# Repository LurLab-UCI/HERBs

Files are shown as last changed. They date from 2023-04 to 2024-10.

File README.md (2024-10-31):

# HERBs
Head-fixed Environment for Rodent Behaviors

This is a comprehensive, affordable and highly flexible hardware-software solution for head-fixed behaviors

For installation instructions and documentation see Wiki (https://github.com/LurLab-UCI/HERBs/wiki)

If used, please cite:
https://www.eneuro.org/content/10/6/ENEURO.0018-23.2023.long

**Critical Update Oct 30, 2024**

HERBs 2.0 is realeased with important bug fixes and communication updates
bug fixes:
* fixed a bug that caused stimulus display to be only half of what was defined in GUI
* fixed bug that caused multiple licks to be printed in the same line
* updated serial communicaton to work with new MATLAB releases

It is recomended that all users switch to HERBs 2.0 for correct stimulus duration.

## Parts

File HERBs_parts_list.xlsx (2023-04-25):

 | # per rig (GNG) | # per rig (2AFC) | ~ price | cost (GNG) | cost (2AFC) | vendor | part # | link
arduino
arduino mega | 1 | 1 | 40.3 | 40.3 | 40.3 | Arduino | A000067 | https://store-usa.arduino.cc/products/arduino-mega-2560-rev3?selectedStore=us
arduino DUE | 1 | 1 | 40.3 | 40.3 | 40.3 | arduino | A000062 | https://store-usa.arduino.cc/products/arduino-due
electronics and other parts
capacitative lick detector | 1 | 3 | 6.5 | 6.5 | 19.5 | sparkfun | 14520 | https://www.sparkfun.com/products/14520
capacitor | 1 | 3 | 0.3 | 0.3 | 0.9 | sparkfun | 8375 | https://www.sparkfun.com/products/8375
power control kit | 1 | 3 | 5.95 | 5.95 | 17.85 | sparkfun | 12959 | https://www.sparkfun.com/products/12959
MOSFET chip (alternative power ctrl.) | 1 | 3 | 1.25 | 1.25 | 3.75 | sparkfun | 10213 | https://www.sparkfun.com/products/10213
level converter | 1 | 1 | 3.5 | 3.5 | 3.5 | sparkfun | BOB-12009 | https://www.sparkfun.com/products/12009
10k Ohm resistor | 1 | 3 | 0.025 | 0.025 | 0.075 | sparkfun | 11508 | https://www.sparkfun.com/products/11508
diode rectifier | 1 | 3 | 0.25 | 0.25 | 0.75 | sparkfun | 14884 | https://www.sparkfun.com/products/14884
speakers | 2 | 2 | 2.45 | 4.9 | 4.9 | sparkfun | 9151 | https://www.sparkfun.com/products/9151
1/4 inch hub | 1 | 1 | 4.99 | 4.99 | 4.99 | sparkfun | 12488 | https://www.sparkfun.com/products/12488
LED panels | 3 | 3 | 6.95 | 20.85 | 20.85 | adafruit | 2973 | https://www.adafruit.com/product/2973
LED panel drivers | 3 | 3 | 5.95 | 17.85 | 17.85 | adafruit | 2946 | https://www.adafruit.com/product/2946
audio amp | 1 | 1 | 19.95 | 19.95 | 19.95 | adafruit | MAX9744 | https://www.adafruit.com/product/1752
tubing (if longer range is needed) | 1 | 1 | 86 | 86 | 86 | cole-parmer | EW-06419-04 | https://www.coleparmer.com/i/masterflex-microbore-transfer-tubing-tygon-nd-100-80-0-040-id-x-0-070-od-100-ft/0641904?searchterm=EW-06419-04
solenoid valve | 1 | 3 | 75.78 | 75.78 | 227.34 | reet corp. | 075P2NC12-02S | http://www.reetcorp.com/products-valves.html
1/4 inch shaft ~1.5'' long | 1 | 1 | 9.64 | 9.64 | 9.64 | McMaster | 8632T144 | https://www.mcmaster.com/8632T144/
1/4 bearings | 2 | 2 | 10.98 | 21.96 | 21.96 | McMaster | 4262T36 | https://www.mcmaster.com/4262T36/
1/4'' wheel lock shaft collar | 1 | 1 | 3.1 | 3.1 | 3.1 | McMaster | 9946K11 | https://www.mcmaster.com/9946K11/
12v power supply | 1 | 1 | 6.98 | 6.98 | 6.98 | amazon | generic | https://www.amazon.com/Adapter-SANSUN-AC100-240V-Transformers-Switching/dp/B01AZLA9XQ
9V power supply | 1 | 1 | 9.99 | 9.99 | 9.99 | amazon | generic | https://www.amazon.com/DAddario-PW-CT-9V-Power-Adapter-Sleeve-Positive/dp/B00191WVF6
running wheel | 1 | 1 | 12.99 | 12.99 | 12.99 | amazon | generic | https://www.amazon.com/gp/product/B00ZB3S62K/ref=ppx_yo_dt_b_search_asin_title?ie=UTF8&psc=1
plasti dip (wheel coating) | 1 | 1 | 7.99 | 7.99 | 7.99 | amazon | generic | https://www.amazon.com/Plasti-Dip-11252-6-Spray-Fluid_Ounces/dp/B00KUBKUQ8?cv_ct_cx=plasti+dip
3D arm | 1 | 1 | 31.35 | 31.35 | 31.35 | amazon | generic | https://www.amazon.com/gp/product/B07KPY6ZC3/ref=ppx_yo_dt_b_search_asin_title?ie=UTF8&psc=1
IR webcam | 1 | 1 | 34.99 | 34.99 | 34.99 | amazon | generic | https://www.amazon.com/gp/product/B0829HZ3Q7/ref=ppx_yo_dt_b_search_asin_title?ie=UTF8&psc=1
power strip (8x) | 1 | 1 | 17.97 | 17.97 | 17.97 | amazon | generic | https://www.amazon.com/Protector-Nuetsa-Extension-Outlets-Joules/dp/B09F2XPJ47?s=electronics
PC (core i5, 8gb ram) | 1 | 1 | 500 | 500 | 500 | amazon | any | https://www.amazon.com/Dell-Inspiron-Compact-Tower-Desktop/dp/B09HHMZN4W?s=electronics
small breadboards | 1 | 1 | 9.59 | 9.59 | 9.59 | amazon | generic | https://www.amazon.com/DEYUE-Solderless-Prototype-Breadboard-breadboard/dp/B07DMHVC3R
20awg wire | 1 | 1 | 16.38 | 16.38 | 16.38 | amazon | generic | https://www.amazon.com/gp/product/B083DNGSPV/ref=ppx_yo_dt_b_search_asin_title?ie=UTF8&psc=1
LED goosneck lamp | 1 | 1 | 21.5 | 21.5 | 21.5 | amazon | generic | https://www.amazon.com/gp/product/B07L6T1N1K/ref=ppx_yo_dt_b_search_asin_title?ie=UTF8&psc=1
spout tubing | 1 | 1 | 7.58 | 7.58 | 7.58 | amazon | generic | https://www.amazon.com/gp/product/B004WPQ59O/ref=ppx_yo_dt_b_search_asin_title?ie=UTF8&psc=1
rotary servo | 1 | 2 | 20.99 | 20.99 | 41.98 | amazon | MG90S | https://www.amazon.com/gp/product/B07F7VJQL5/ref=ppx_yo_dt_b_search_asin_title?ie=UTF8&psc=1
linear actuator (optional if not servo) | 1 | 2 | 90 | 90 | 180 | actuonix | L12-30-50-12-I | https://www.actuonix.com/Rod-Actuators-s/1924.htm
mechanical parts
90 degree thumbscrew holder (RA90) | 4 | 4 | 10.3 | 41.2 | 41.2 | Thorlabs | RA90 | https://www.thorlabs.com/thorproduct.cfm?partnumber=RA90
adjustable angle thumbscrew holder | 2 | 2 | 25.63 | 51.26 | 51.26 | Thorlabs | SWC | https://www.thorlabs.com/thorproduct.cfm?partnumber=SWC
1/2'' rod to screw (RA180) | 1 | 1 | 11.75 | 11.75 | 11.75 | Thorlabs | RA180 | https://www.thorlabs.com/thorproduct.cfm?partnumber=RA180
1/2' rod 1'' (TR1) | 1 | 1 | 5.12 | 5.12 | 5.12 | Thorlabs | TR1 | https://www.thorlabs.com/newgrouppage9.cfm?objectgroup_id=1266&pn=TR1#237
1/2' rod 2'' (TR2) | 1 | 1 | 5.62 | 5.62 | 5.62 | Thorlabs | TR2 | https://www.thorlabs.com/newgrouppage9.cfm?objectgroup_id=1266&pn=TR1#237
1/2' rod 4'' (TR4) | 3 | 3 | 6.35 | 19.05 | 19.05 | Thorlabs | TR4 | https://www.thorlabs.com/newgrouppage9.cfm?objectgroup_id=1266&pn=TR1#237
1/2' rod 6'' (TR6) | 4 | 4 | 7.7 | 30.8 | 30.8 | Thorlabs | TR6 | https://www.thorlabs.com/newgrouppage9.cfm?objectgroup_id=1266&pn=TR1#237
1/2' rod 8'' (TR8) | 1 | 1 | 9.23 | 9.23 | 9.23 | Thorlabs | TR8 | https://www.thorlabs.com/newgrouppage9.cfm?objectgroup_id=1266&pn=TR1#237
post holder base full (BA1) | 4 | 4 | 5.77 | 23.08 | 23.08 | Thorlabs | BA1 | https://www.thorlabs.com/newgrouppage9.cfm?objectgroup_id=47&pn=BA1#2978
post holder base half (BA1S) | 2 | 2 | 5.36 | 10.72 | 10.72 | Thorlabs | BA1S | https://www.thorlabs.com/newgrouppage9.cfm?objectgroup_id=47&pn=BA1#2978
post holders 1 inch | 1 | 1 | 7.78 | 7.78 | 7.78 | Thorlabs | PH1 | https://www.thorlabs.com/newgrouppage9.cfm?objectgroup_id=1268&pn=PH1#238
post holders 2 inch | 2 | 2 | 8.52 | 17.04 | 17.04 | Thorlabs | PH2 | https://www.thorlabs.com/newgrouppage9.cfm?objectgroup_id=1268&pn=PH1#238
post holders 3 inch | 2 | 2 | 9.16 | 18.32 | 18.32 | Thorlabs | PH3 | https://www.thorlabs.com/newgrouppage9.cfm?objectgroup_id=1268&pn=PH1#238
mini series adapter | 2 | 2 | 5.55 | 11.1 | 11.1 | Thorlabs | MSA8 | https://www.thorlabs.com/newgrouppage9.cfm?objectgroup_id=1745&pn=MSA8#1438
90 degree bracket | 2 | 2 | 15.53 | 31.06 | 31.06 | Thorlabs | ER90B | https://www.thorlabs.com/newgrouppage9.cfm?objectgroup_id=6324&pn=ER90B#6332
cage assembly rod | 2 | 2 | 5.33 | 10.66 | 10.66 | Thorlabs | ER05 | https://www.thorlabs.com/newgrouppage9.cfm?objectgroup_id=4125&pn=ER05#4143
3D stage | 1 | 1 | 336.08 | 336.08 | 336.08 | Thorlabs | DT12XYZ | https://www.thorlabs.com/newgrouppage9.cfm?objectgroup_id=2952&pn=DT12XYZ
breadboard 12/16 | 1 | 1 | 204.43 | 204.43 | 204.43 | Thorlabs | MB1218 | https://www.thorlabs.com/newgrouppage9.cfm?objectgroup_id=159&pn=MB1218
machined / printed parts
LED panel holder | 1 | 1 |  |  |  | lab made: either 3d print or bend a piece of aluminium (also possible to carve from styrofoam
tripple spout holder | 0 | 1 |  |  |  | lab made: either 3d print or carve from styrofoam
servo-to-linear-actuator translator | 1 | 2 |  |  |  | lab made: 3D print
data acqusition
Nationl Instruments DAQ (alternative) | 1 | 1 | 1897 | 1897 | 1897 | National instruments | USB-6218 | https://www.ni.com/en-us/shop/hardware/products/multifunction-io-device.html
MC USB-1208FS-Plus (low cost) | 1 | 1 | 199 | 199 | 199 | Measurement Computing | 6069-410-061 | https://www.mccdaq.com/usb-data-acquisition/USB-1208FS-Plus.aspx
enclosure (double rig) - costs approximate
1 3/8'' dovel for frame 12'' long | 8 | 8
1 3/8'' dovel for frame 24'' long | 6 | 6
1 3/8'' dovel for frame 18'' long | 6 | 6
1 3/8'' dovel 8ft cut to above sizes | 5 | 5 | 7.98 | 39.9 | 39.9 | home depot | generic | https://www.homedepot.com/p/Mendocino-Forest-Products-1-3-8-in-x-1-3-8-in-x-8-ft-B-and-Better-S4S-Redwood-Lumber-903116/100038906
1/2'' plywood 21x24'' for tops | 3
1/2'' plywood 14x11'' for doors | 4
1/2'' plywood 30x24'' for back | 1
1/2'' plywood 30x21'' for sides | 2
1/2'' plywood 4' x 8' cut to above size | 1 | 1 | 60 | 60 | 60 | home depot | generic | https://www.homedepot.com/p/Columbia-Forest-Products-1-2-in-x-4-ft-x-8-ft-PureBond-Birch-Plywood-833185/100020218?MERCH=REC-_-searchViewed-_-NA-_-100020218-_-N
door hinges | 8 | 8 | 3.98 | 31.84 | 31.84 | amazon | generic | https://www.amazon.com/LIBERTY-H01915C-SN-2-Inch-Semi-Wrap-Overlay/dp/B005YVKMR6?s=hi
door magnets (set of 4) | 2 | 2 | 5.98 | 11.96 | 11.96 | amazon | generic | https://www.amazon.com/JQK-Magnetic-Stainless-Thickness-Furniture/dp/B07B4TW3YY?cv_ct_cx=door+magnet&s=hi
2'' wood screws (box) | 1 | 1 | 12.88 | 12.88 | 12.88 | amazon | generic | https://www.amazon.com/gp/product/B08MDXC1GG/ref=ppx_yo_dt_b_search_asin_title?ie=UTF8&psc=1
0.5'' truss head wood screws (box) | 1 | 1 | 6.5 | 6.5 | 6.5 | amazon | generic | https://www.amazon.com/gp/product/B08545BSYB/ref=ppx_yo_dt_b_search_asin_title?ie=UTF8&psc=1
egg crate foam | 1 | 1 | 18.99 | 18.99 | 18.99 | amazon | generic | https://www.amazon.com/Polyurethane-Charcoal-Convoluted-Foam-Packing/dp/B01G61TJCG?s=musical-instruments
mass loaded vinyl | 1 | 2 | 59.99 | 59.99 | 119.98 | amazon | generic | https://www.amazon.com/TMS-Sound-Proofing-Padding-Wall/dp/B01EGX3XF0?cv_ct_cx=mass%2Bloaded%2Bvinyl
 |  |  | sum | 2341.105 | 2590.295

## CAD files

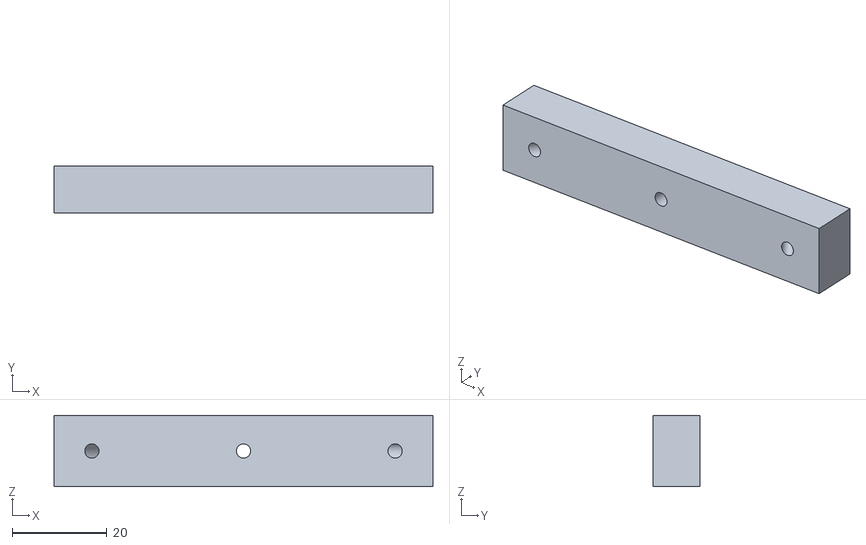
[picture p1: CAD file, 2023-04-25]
3D files/spout-holder-for-linear-actuator.STL
80.0 x 10.00 x 15.0

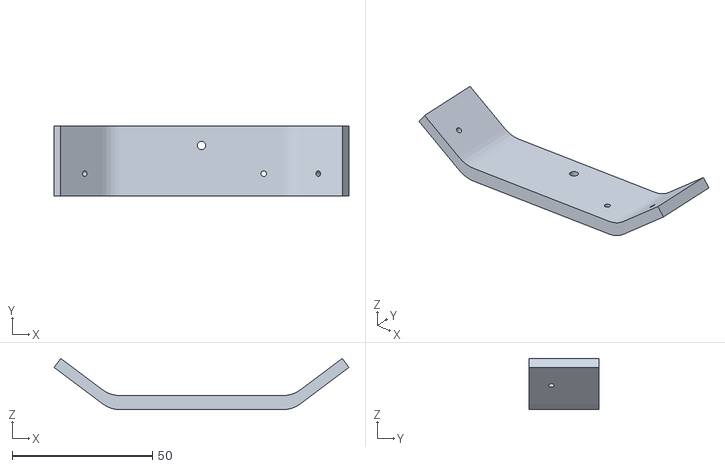
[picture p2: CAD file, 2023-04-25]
3D files/LED-panel-holder.STL
105.0 x 25.0 x 18.2

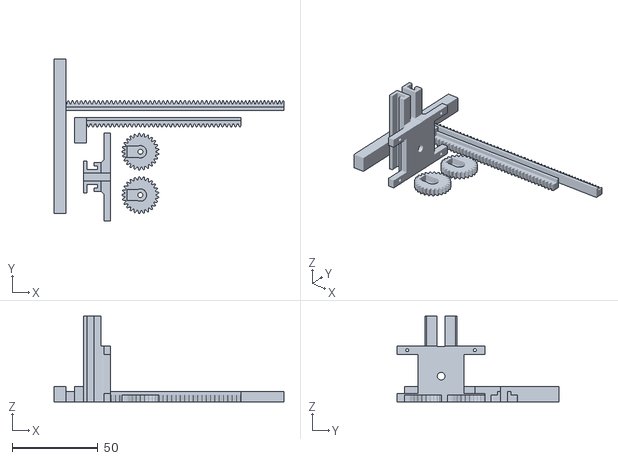
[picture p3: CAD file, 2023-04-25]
3D files/servo-to-linear-actuator-translator.stl
133.8 x 94.3 x 50.0

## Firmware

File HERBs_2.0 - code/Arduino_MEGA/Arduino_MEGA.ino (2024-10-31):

//#define DEBUG

// define this with full rig (all the DACs)
#define FULL_RIG
// SIMPLE_RIG is a rig with no singler dac
//#define SIMPLE_RIG
//define this if running matlab that handles fractional reward durations
//#define FRACTIONAL_REWARD_DURATION

/*
 IF USING SERVO_TIMERS_45 
CENTER servo connected to pin 8
LR servo connected to pin 46
DUE reset connected to pin 28
  OTHERWISE
CENTER servo connected to pin 6
LR servo connected to pin 7
DUE reset connected to pin 8
*/

#define SERVO_TIMERS_45

#ifdef SERVO_TIMERS_45
  #include <Servo_Hardware_PWM.h>
  Servo myServoC;
  Servo myServoLR;
 #else
  #include <Servo.h>
  Servo myservoC;
  Servo myservoLR;
 #endif 


// define this if audio amp not available
//#define NO_AUDIO_AMPLIFIER

//define light panels used
#define LEFT_LED_PANEL
#define CENTER_LED_PANEL
#define RIGHT_LED_PANEL
                                    
#include <MsTimer2.h>
#include "TimerThree.h"
#include <Wire.h>
#include <Adafruit_GFX.h>
#include <Adafruit_IS31FL3731.h>
#include <Adafruit_MCP4728.h>
#include <Adafruit_MCP4725.h>


//  light panels  ------------------------------------
// light panel i2c addresses
uint16_t Left_Panel =  0x76;
uint16_t Center_Panel =  0x74;
uint16_t Right_Panel =  0x75;

Adafruit_IS31FL3731 ledmatrixL = Adafruit_IS31FL3731();
Adafruit_IS31FL3731 ledmatrixC = Adafruit_IS31FL3731();
Adafruit_IS31FL3731 ledmatrixR = Adafruit_IS31FL3731();

//  dacs  ------------------------------------
Adafruit_MCP4728 dac;
Adafruit_MCP4725 dac_single;

//-------------------------------------------------------------------------------
// DAC signal level definitions for channels C and D

#define C_

#define tbyte1_Panel_C  2500
#define tbyte0_Panel_C  2000
#define tbyte4_Panel_C  1800   // full panel

#define tbyte1_Panel_R  3500
#define tbyte0_Panel_R  3000
#define tbyte5_Panel_R  4000
#define tbyte4_Panel_R  4000   // full panel

#define tbyte1_Panel_L  1500
#define tbyte0_Panel_L  1000
#define tbyte5_Panel_L  0500
#define tbyte4_Panel_L  0250    //full panel

#define left_right_vertical_L       0500
#define right_to_left_vertical_L    1000
#define bottom_to_top_horizontal_L  1500
#define top_to_bottom_horizontal_L  2000

#define left_right_vertical_R       2500
#define right_to_left_vertical_R    3000
#define bottom_to_top_horizontal_R  3500
#define top_to_bottom_horizontal_R  4000

// combo mode
#define stripes_horizontal_L        500  
#define stripes_vertical_L          1000  
#define stripes_angled_P45_L        1500  
#define stripes_angled_M45_L        2000  
#define stripes_horizontal_R        2500  
#define stripes_vertical_R          3000  
#define stripes_angled_P45_R        3500  
#define stripes_angled_M45_R        4000  
 
// reward indicator values
#define D_reward_L 1000   // 1000 mV
#define D_reward_C 2000
#define D_reward_R 3000

//  audio amp  ------------------------------------
#define MAX9744_I2CADDR 0x4B

// ---------------------------------------------------------------------------------
//    memory allocations

uint16_t x0 = 0;
uint16_t y0 = 15;
uint16_t lp = 0;
uint32_t  reward_pulse_C = 0; 
uint32_t  reward_pulse_R = 0; 
uint32_t  reward_pulse_L = 0; 
uint32_t  airpuff_pulse = 0; 
uint32_t  light_pattern_speed = 20;
uint8_t  light_pattern_brightness = 4;
uint32_t  tre = 0;

int8_t  vol = 0; 
int8_t  oldvol = 5; 
int8_t  int_flag1 = 0; 
int8_t  int_flag2 = 0; 
int8_t  int_flag3 = 0; 
int8_t int_active = 0;

uint16_t temp = 0;
uint16_t temp1 = 0;
uint16_t temp2 = 0;
uint16_t temp3 = 0;
uint16_t temp4 = 0;
uint32_t int_disable_start = 0;
uint32_t temp_time = 0;
uint8_t tempbyte = 0;
uint8_t dac_val = 0;
uint16_t dac_val_audio = 0;

uint16_t mbank;
uint16_t ontime;
uint16_t offtime;

uint16_t to_due;

int8_t  int1_lvl = 0; 
int8_t  int2_lvl = 0; 
int8_t  int3_lvl = 0; 
int8_t  int1_lvl_old = 0; 
int8_t  int2_lvl_old = 0; 
int8_t  int3_lvl_old = 0; 
uint8_t  temp_byte = 0; 
uint8_t  temp_byte1 = 0; 
uint8_t  left_right_flag = 0;
uint8_t  noise_tone_flag = 0;
uint8_t  panel_mode = 0;
uint8_t  panel_mode_L = 0;
uint8_t  panel_mode_R = 0;
uint8_t  panel_mode_C = 0;

uint8_t bright_dark_L = 7;
uint8_t bright_dark_R = 7;
uint8_t single_panel_L = 0;
uint8_t single_panel_R = 0;
uint8_t light_tone_flag = 0;

uint16_t visual_half_cycle = 0;
uint16_t auditory_half_cycle = 0;
uint8_t  number_of_visual_cycles = 0;
uint8_t  number_of_auditory_cycles = 0;
uint32_t visual_cycle_start = 0;
uint32_t auditory_cycle_start = 0;
uint8_t audio_on = 0;
uint8_t visual_on = 0;

uint8_t  left_right_flag_visual = 0;
uint8_t  left_right_flag_auditory = 0;
uint16_t visual_start_delay = 0;
uint16_t auditory_start_delay = 0;

uint32_t visual_delay_start_time = 0;
uint8_t  visual_start_pending = 0;  
uint32_t auditory_delay_start_time = 0;
uint8_t  auditory_start_pending = 0;  

uint8_t skip = 1;
uint8_t tb0 = 0;
uint8_t tb1 = 0;
uint8_t tb2 = 0;
uint8_t tb3 = 0;
uint8_t CHC_zeroflag = 0;
uint8_t CHD_zeroflag = 0;

// for Decision Making
uint16_t visual_low_cycle_L = 0;
uint16_t visual_high_cycle_L = 0;
uint16_t visual_low_cycle_R = 0;
uint16_t visual_high_cycle_R = 0;
uint16_t visual_low_cycle_C = 0;
uint16_t visual_high_cycle_C = 0;
uint8_t  number_of_visual_cycles_L = 0;
uint8_t  number_of_visual_cycles_R = 0;
uint8_t  number_of_visual_cycles_C = 0;
uint32_t visual_cycle_start_L = 0;
uint32_t visual_cycle_start_R = 0;
uint32_t visual_cycle_start_C = 0;
uint8_t cycle_type_L = 0;
uint8_t cycle_type_R = 0;
uint8_t cycle_type_C = 0;

uint16_t auditory_low_cycle_L = 0;
uint16_t auditory_high_cycle_L = 0;
uint16_t auditory_low_cycle_R = 0;
uint16_t auditory_high_cycle_R = 0;
uint8_t  number_of_auditory_cycles_L = 0;
uint8_t  number_of_auditory_cycles_R = 0;
uint32_t auditory_cycle_start_L = 0;
uint32_t auditory_cycle_start_R = 0;
uint8_t  mbank_L = 0;
uint8_t  mbank_R = 0;
uint8_t cycle_type_auditory_L = 0;
uint8_t cycle_type_auditory_R = 0;

uint8_t nstripes_L = 1;
uint8_t nstripes_R = 1;

volatile byte state = LOW;
uint8_t  xstart = 3;
uint8_t  ystart = 0;
uint8_t  xstop = 6;
uint8_t  ystop = 8;
uint8_t  noise_active = 0;
uint32_t pwidth = 100;
uint16_t debounce_count = 0;

uint8_t  light_panels_present = 0;

uint8_t tl;
uint8_t th;


//=========================================================
//pin assignments
const byte Tone0 = 47;  
const byte Tone1 = 49;  
const byte AirPuff = 48;
const byte RewardL = 50;  
const byte RewardR = 51;  
const byte RewardC = 52;  
const byte Test1   = 34;  
const byte light_panel_signal_L = 38;  
const byte light_panel_signal_R = 40;  


const byte reset_indicator = 44;  
const byte lick_indicator_C = 10;
const byte LickCenter = 18;
const byte LickRight = 19;
const byte lick_indicator_R = 11;
const byte LickLeft = 2;
const byte lick_indicator_L = 12;
const byte cclockpin = 22;     // default to pin 13

#ifdef SERVO_TIMERS_45
  const byte due_reset = 28;
#else
  const byte due_reset = 8;
#endif

const byte dac_write_indicator = 33;
const byte dac_write_indicator_audio = 35;
const byte response_window_indicator = 37;
const byte audio_mute = 44;


//end of pin assignments
//=========================================================
// serial receive character decode functions

//    'a'  set audio volume
//    'b'  DM Left panel mode
//    'c'  write to dac
//    'd'  send air puff
//    'e'  tone 0 on/off
//    'f'  tone 1 on/off
//    'g'  write to single dac
//    'i'  move actuator 1
//    'j'  move actuator 2
//    'k'  valve control
//    'l'  auditory sequence
//    'm'  DM left audio   
//    'n'  DM right audio     
//    'o'  response_window_indicator
//    'p'  enable interrupts
//    'q'  reward duration C
//    'r'  Light Panel  Control
//    's'
//    't'  audio off
//    'u'  air puff pulse duration
//    'v'  reward duration L
//    'w'  reward duration R
//    'x'  reward R
//    'y'  reward L
//    'z'  reward C
//    '?'  left/right flag
//    '{'  light_pattern_speed
//    '}'  light_pattern_brightness
//    '('  moving bars mode
//    '#'  Pulse durations
//    '^'  test print
//    '~'
//    '!'  enable interrupts
//    '@'  small panels to dark state
//    '$'
//    '%'
//    '&'  DM Center panel mode
//    ')'
//    '+'  DM Right panel mode
//    '-'  sensory Stimulus panel mode
//    '='  set tone frequency
//    '['
//    ']'
//    '\'
//    ';'  light panel initialization control
//    ':'  stop all timers and lights snd audio
//    '''
//    '"'  initialize light panels for gonogo
//    ','
//    '.'
//    '/'
//    '<'
//    '>'
//=========================================================

#define pg_dark 7
#define pg_small 3
#define pg_full 4


//============================================================================
// standard Arduino setup()

void setup()
{
  
    pinMode(due_reset, OUTPUT);
    pinMode(Tone0, OUTPUT);
    pinMode(Tone1, OUTPUT);
    pinMode(RewardL, OUTPUT);
    pinMode(RewardC, OUTPUT);
    pinMode(RewardR, OUTPUT);
    pinMode(AirPuff, OUTPUT);
    pinMode(cclockpin, OUTPUT);
    pinMode(reset_indicator, OUTPUT);
    pinMode(dac_write_indicator, OUTPUT);
    pinMode(dac_write_indicator_audio, OUTPUT);
    pinMode(response_window_indicator, OUTPUT);
    pinMode(Test1, OUTPUT);
    pinMode(light_panel_signal_L, OUTPUT);
    pinMode(light_panel_signal_R, OUTPUT);
    
    digitalWrite(due_reset, LOW);
    digitalWrite(Test1, LOW);
    digitalWrite(light_panel_signal_L, LOW);
    digitalWrite(light_panel_signal_R, LOW);
    digitalWrite(response_window_indicator, LOW);
    
    digitalWrite(Tone0, LOW);   // turn the LED on (HIGH is the voltage level)
    digitalWrite(Tone1, LOW);   // turn the LED on (HIGH is the voltage level)
    digitalWrite(RewardL, LOW);   // turn the LED on (HIGH is the voltage level)
    digitalWrite(RewardC, LOW);   // turn the LED on (HIGH is the voltage level)
    digitalWrite(RewardR, LOW);   // turn the LED on (HIGH is the voltage level)
    digitalWrite(AirPuff, LOW);   // turn the LED on (HIGH is the voltage level)
    digitalWrite(reset_indicator, LOW);   // turn the LED on (HIGH is the voltage level)
    digitalWrite(dac_write_indicator, LOW);   
    digitalWrite(dac_write_indicator_audio, LOW);   


    while (!Serial);
    delay(100);
    Wire.begin();    
    Serial.begin(115200);
    Serial3.begin(115200);

    

    pinMode(LickCenter, INPUT_PULLUP);
    pinMode(LickRight, INPUT_PULLUP);
    pinMode(LickLeft, INPUT_PULLUP);
    pinMode(lick_indicator_C, OUTPUT);
    pinMode(lick_indicator_R, OUTPUT);
    pinMode(lick_indicator_L, OUTPUT);
    digitalWrite(lick_indicator_C, LOW);
    digitalWrite(lick_indicator_R, LOW);
    digitalWrite(lick_indicator_L, LOW);

    attachInterrupt(digitalPinToInterrupt(LickCenter), lick1, RISING);
    attachInterrupt(digitalPinToInterrupt(LickRight), lick2, RISING);
    attachInterrupt(digitalPinToInterrupt(LickLeft), lick3, RISING);

    int1_lvl = digitalRead(LickCenter);
    int1_lvl_old = digitalRead(LickCenter);
    int2_lvl = digitalRead(LickRight);
    int2_lvl_old = digitalRead(LickRight);
    int3_lvl = digitalRead(LickLeft);
    int3_lvl_old = digitalRead(LickLeft);

   

//=======================================================
//attach the two servos
#ifdef SERVO_TIMERS_45
  myServoC.attach(8);  // attaches the servo on pin 8 to the servo object
  myServoLR.attach(46);  // attaches the servo on pin 46 to the servo object
//force servos to full retract
  temp = 180;
  myServoC.write(temp);              // 
  temp = 0;
  myServoLR.write(temp);              // 
#else
  myservoC.attach(6);  // attaches the servo on pin 8 to the servo object
  myservoLR.attach(7);  // attaches the servo on pin 46 to the servo object
//force servos to full retract
  temp = 180;
  myservoC.write(temp);              // 
  temp = 0;
  myservoLR.write(temp);              // 
#endif

   
//=======================================================
//  set volume to 0 on power-up
  vol = 0;
  setvolume(vol);
  

// connection to light panels
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

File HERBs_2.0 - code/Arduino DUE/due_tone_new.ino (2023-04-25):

#define oneHzSample 1000000/maxSamplesNum  // sample for the 1Hz signal expressed in microseconds

// Include the required Wire library for I2C
#include <Wire.h>
#include <Tone.h>



#define  SAMPLES   32
#define  NSAMPLES   8192
#define  CEILING   4096
uint16_t wav0[SAMPLES];
uint16_t wav1[SAMPLES];
uint16_t wavn0[NSAMPLES];
uint16_t wavn1[NSAMPLES];
uint16_t temp = 0;
float   tfl = 0;  
String volume = "VOLUME";
String str = "12";

uint8_t noise_flag = 0;
uint8_t signal_off = 0;
uint8_t fpointer = 0;

int8_t up_down_freq = 0;
int8_t left_right = 0;

int8_t column = 0;


uint16_t timer = 0;
uint32_t timer_start = 0;
uint8_t signal_or_delay = 0; 

// frequency pars
#define  NCHAR  16
#define  NITEMS  10
char* freqstr[][NCHAR]={" Noise           "," 2 kHz          ", " 4 kHz          " " 6 kHz          ", " 8 kHz          ",
"12 kHz          ", "16 kHz          ","24 kHz          ","32 kHz          ","Random          "};
float freq[9] = {1000,2000,4000,6000,8000,12000,16000,24000,32000};

// volume pars
#define  N_VOL_ITEMS  44
int8_t up_down_vol = 0;
uint8_t rbyte = 0;





//Tone tone1;
int x = 0;
int y = 0;
byte skip = 1;

uint8_t flag = 1;

volatile int wave0 = 0, wave1 = 1;
volatile int wave2 = 2, wave3 = 3;
int wavel = 0, waver = 0;

const byte tout = 31;  
const byte tonepin = 3;  

int i = 0;
int sample;


void setup() {


  analogWriteResolution(12);  // set the analog output resolution to 12 bit (4096 levels)
  pinMode(tout, OUTPUT);
  digitalWrite(tout, LOW);  
  pinMode(3, OUTPUT);
  //digitalWrite(3, LOW);  


  CreateSineWaveTable0();
  CreateSineWaveTable1();
  CreateNoise();
  
  setupDAC();
  float freq_hz = 32000; // Target: 200kHz
  setupTC(freq_hz);
  NVIC_EnableIRQ(DACC_IRQn);


  Serial.begin(115200);

  // Start the I2C Bus as Slave on address 9
  Wire.begin(9); 
  // Attach a function to trigger when something is received.
  Wire.onReceive(receiveEvent);
  
}
void loop() {}
 
      
void receiveEvent(int bytes) 
{
    //digitalWrite(tout, HIGH);  

  x = Wire.read();    // read one character from the I2C
  y = Wire.read();    // read one character from the I2C
  skip = Wire.read();    // read one character from the I2C
  Serial.print(x);
  Serial.print(y);
  Serial.print(skip);
  Serial.println("-----");


dacc_set_channel_selection(DACC, 0);
dacc_disable_channel(DACC, 0);
dacc_set_channel_selection(DACC, 1);
dacc_disable_channel(DACC, 1);


if (y==2)    //TURN NOISE ON
  {

      if (x == 1)
      {
       dacc_set_channel_selection(DACC, 0);
       dacc_enable_channel(DACC, 0);
      }
      else
      {
       dacc_set_channel_selection(DACC, 1);
       dacc_enable_channel(DACC, 1);
      }
      fpointer = 0;
      update_frequency();            
      return;
  }
  else
  {
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
